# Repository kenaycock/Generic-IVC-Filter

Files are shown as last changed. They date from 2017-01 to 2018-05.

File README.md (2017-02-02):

# Generic-IVC-Filter
*Design of a Generic IVC Filter*

======================

RESOURCES
---------

1. **CAD/** SolidWorks 3D solid models and 2D drawings of the generic IVC filter

2. **Fatigue_coupon/** Placeholder for files relating to fatigue coupon specimens

3. **Preliminary_FEA/** ABAQUS simulation files for predicting fatigue performance of the generic IVC filter

4. **Regulatory-grade_FEA/** Placeholder for final FEA simulation files

5. **.pdf** Further documentation 

CREDIT
------
US FDA: Brent Craven, Jason Weaver, Kenneth Aycock

Confluent Medical (formerly NDC): Tom Duerig, Craig Bonsignore, Karthikeyan Senthilnathan

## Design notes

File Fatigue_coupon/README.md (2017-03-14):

# Fatigue coupon

*Placeholder for files relating to design, manufacture, and testing of fatigue coupons (aka "subcomponent" models)*

- [x] Design fatigue coupon
- [x] Design coupon fixture
- [x] Perform FEA analyses to predict the stresses in the coupon -- do they mimic the *in vivo* loading of the device?
- [x] Generate drawings and DXF for coupon
- [x] Upload files
- [ ] Feedback?

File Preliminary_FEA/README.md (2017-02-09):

# Preliminary FEA

*ABAQUS FEA simulation files*

1. **Input_Files/**   ABAQUS/Standard input files (includes mesh, material properties, boundary conditions, etc.)

2. **ABAQUS_CAE/**   ABAQUS/CAE files used to generate ABAQUS input

3. **Generic_IVC_filter_project_Preliminary_FEA_Summary.pdf**   Brief documentation of preliminary FEA simulation results

Simulations were performed using the same material constants for the ABAQUS Superelastic UMAT as those in  https://github.com/cbonsig/strain-amplitude-volume-fraction/blob/master/Abaqus_6.12-1_Example.inp

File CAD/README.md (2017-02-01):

# CAD

*Directories/Files:*

1. **Rev0** Starting design for generic IVC filter

2. **Rev1** Generic IVC filter following design revision and preliminary FEA analysis. This model needs to be revised now for manufacturing a prototype (adjust kerf, etc.).

3. **Rev1.1** Rev1 modified for manufacturing

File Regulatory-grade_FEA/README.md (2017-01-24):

# Regulatory-grade FEA

*Placeholder for final, "regulatory-grade" FEA simulations*

Todo:
V&V:

1. Verification
  - [ ] Code verification? (i.e., MMS?)
  - [ ] Numerical verification (i.e., grid refinement study)
  - [ ] Material model verification: in collaboration with Confluent Medical, 
    - [ ] obtain lot-specific nitinol material properties
    - [ ] fit constants to raw material testing data 
    
2. Validation
  1. Fatigue testing with sub-component model
    - same material processing history as prototype devices (e.g., heat treating and electropolishing)
  2. Other?

Generic IVCF FEA:

1. Determine final geometry of generic IVC filter
  - [ ] Account for differences between design and manufactured prototypes (tolerances?)
  - [ ] Account for material removed during finishing processes (e.g., electropolishing)
2. Simulate sheathing (prestrain)
3. Simulate placement (contact area/length/forces)
  - [ ] Finalize IVC diameters used to represent variability in human population
4. Valsalva (fatigue)
  - [ ] Finalize boundary conditions (CI=0.5?)

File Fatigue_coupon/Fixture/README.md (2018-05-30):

## Custom fixture used for force-displacement and fatigue tests.

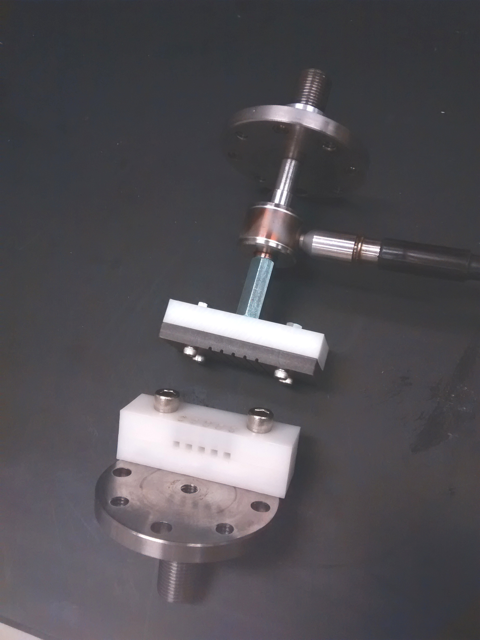
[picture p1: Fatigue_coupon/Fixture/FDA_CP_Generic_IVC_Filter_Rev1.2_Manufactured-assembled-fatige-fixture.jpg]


***Note**: During the experiments, the smooth side of the contact plate (part 5) was used rather than the slotted side due to difficulty alligning the struts with the slots. No lateral motion of the struts was observed during the experiments (confirmed using high-speed video).*

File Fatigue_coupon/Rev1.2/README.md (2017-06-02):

# Fatigue coupons

Experimental plan: 

|                  | <sup>\*</sup>low-strain coupon | <sup>†</sup>high-strain coupon                |
| ---------------- | ----------------- | --------------------------------- |
| strain amplitude | <sup>‡</sup>0.19%, 0.50%      | 0.50%, 0.75%, 1.00%, 1.25%, 1.50% |

<sup>\*</sup>*test to 10<sup>7</sup> cycles*<br>
<sup>†</sup>*fatigue-to-fracture*<br>
<sup>‡</sup>*worst-case physiological conditions, i.e., Valsalva in 28mm IVC*

10 samples per condition:
* 20 low-strain coupons
* 50 high-strain coupons

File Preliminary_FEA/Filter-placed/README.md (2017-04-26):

# Mesh for placed GIVCF

STL meshes for the generic IVC filter placed in a 28 mm-diameter circular vena cava model. 

Virtual filter placement was performed using nonlinear finite element analysis with nitinol material constants from experimental data (see material characterization folder). The vein model was approximated as rigid. 

Dimensions are mm.

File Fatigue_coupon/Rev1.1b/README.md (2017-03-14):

# Rev1.1b

* Proposed fatigue coupon and fatigue fixture assembly
* Equipment: Bose ElectroForce (ELF) 3300
* Tests will be performed inside a fluid bath at 37°C

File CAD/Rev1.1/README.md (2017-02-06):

# Rev1.1

**Rev1 filter revised for manufacturability**

REVISIONS
---------
- [x] Account for
    1. laser beam cutting width (kerf) and
    2. material removal related to surface finishing (see *Open Stent* manuscript from C. Bonsignore for details)
- [x] Change the tubing from TSE0800X0525GS to TSE0800X0515GS to increase the wall thickness and compensate for material removed during surface finishing
    * same OD, new ID (1.3081mm here vs. 1.3335mm in Rev1; see https://shop.confluentmedical.com/collections/tube)
- [x] Add a flat configuration for the laser toolpath
- [x] Improve the drawing sheets
- [x] Create 2D "dxf" file for the laser toolpath (scale is 1:1)

NOTES
-----
* The following values were assumed based on those given in the *Open Stent* manuscript:
    * Laser kerf: ~~0.025mm~~ 0.050mm
    * Material removal during finishing
        * width: ~~0.036mm (i.e., 0.018mm from each side)~~ 0.025mm (i.e., 0.0125mm from each side)
        * thickness: ~~0.059mm (from *inside* surface to remove draw lines)~~ **TBD; measure finished prototypes**

CORRESPONDENCE
--------------
See https://github.com/kenaycock/Generic-IVC-Filter/issues/2

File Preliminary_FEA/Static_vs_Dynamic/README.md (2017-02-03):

# Static vs Dynamic

*Demonstration of a case where the static solver diverges while the dynamic solver converges:*

**Boundary conditions during Valsalva:**
  - Filter hub: **translation constrained in 'y' and 'z', but not in the axial direction, 'x'.**
  - Plate: fixed displacement representing reduction in the minor diameter of the IVC during the Valsalva maneuver
  - Distal end of filter strut: unconstrained, but there is a contact interaction between the strut surface and the plate that represents the vein wall.
    - Tangential friction is set relatively high (0.2); distal end of filter strut *"rocks"* along plate surface
  - **Files:**
    1. ...Static_BCs1.inp (diverges during step 3, 'valsalva1') 
    2. ...Dynamic_BCs1.inp 

<br><br>
*If the boundary conditions are tweaked slightly, the static simulation converges:*

**Boundary conditions during Valsalva:**
  - Filter hub: **translation constrained in 'x', 'y' and 'z' directions.**
  - Plate: fixed displacement representing reduction in the minor diameter of the IVC during the Valsalva maneuver
  - Distal end of filter strut: unconstrained, but there is a contact interaction (including tangential friction) between the strut surface and the plate that represents the vein wall.
    - Tangential friction is set relatively low (0.02); distal end of filter strut *slides* along plate surface
  - **Files:**
    1. ...Static_BCs2.inp
    
<br><br>
CORRESPONDENCE
--------------
**Feedback from Karthik:**
  - Static solver will not converge when there is unconstrained rigid body motion. Adjust boundary conditions accordingly in the future, or use Dynamic/Implicit and ensure that kinetic energy is a small (\<\<1%) fraction of the total internal energy.

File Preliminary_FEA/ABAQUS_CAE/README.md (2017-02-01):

# ABAQUS CAE files

1. **...cae/jnl** ABAQUS/CAE files for preliminary FEA simulations
2. **GIVCF_Rev1.STEP**   3D solid CAD model of the generic IVC filter (exported from SolidWorks); used to generate the finite element meshes in ABAQUS/CAE

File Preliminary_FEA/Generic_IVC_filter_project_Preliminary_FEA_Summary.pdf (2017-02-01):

# Design of a Generic IVC Filter

2/1/2017

Generic IVC Filter Critical Path Project
Kenny Aycock, Jason Weaver and Brent Craven (FDA)
Craig Bonsignore and Tom Duerig (Confluent Medical) | 1

# Summary of Preliminary FEA

# FEA performed to evaluate filter design

### Setup:

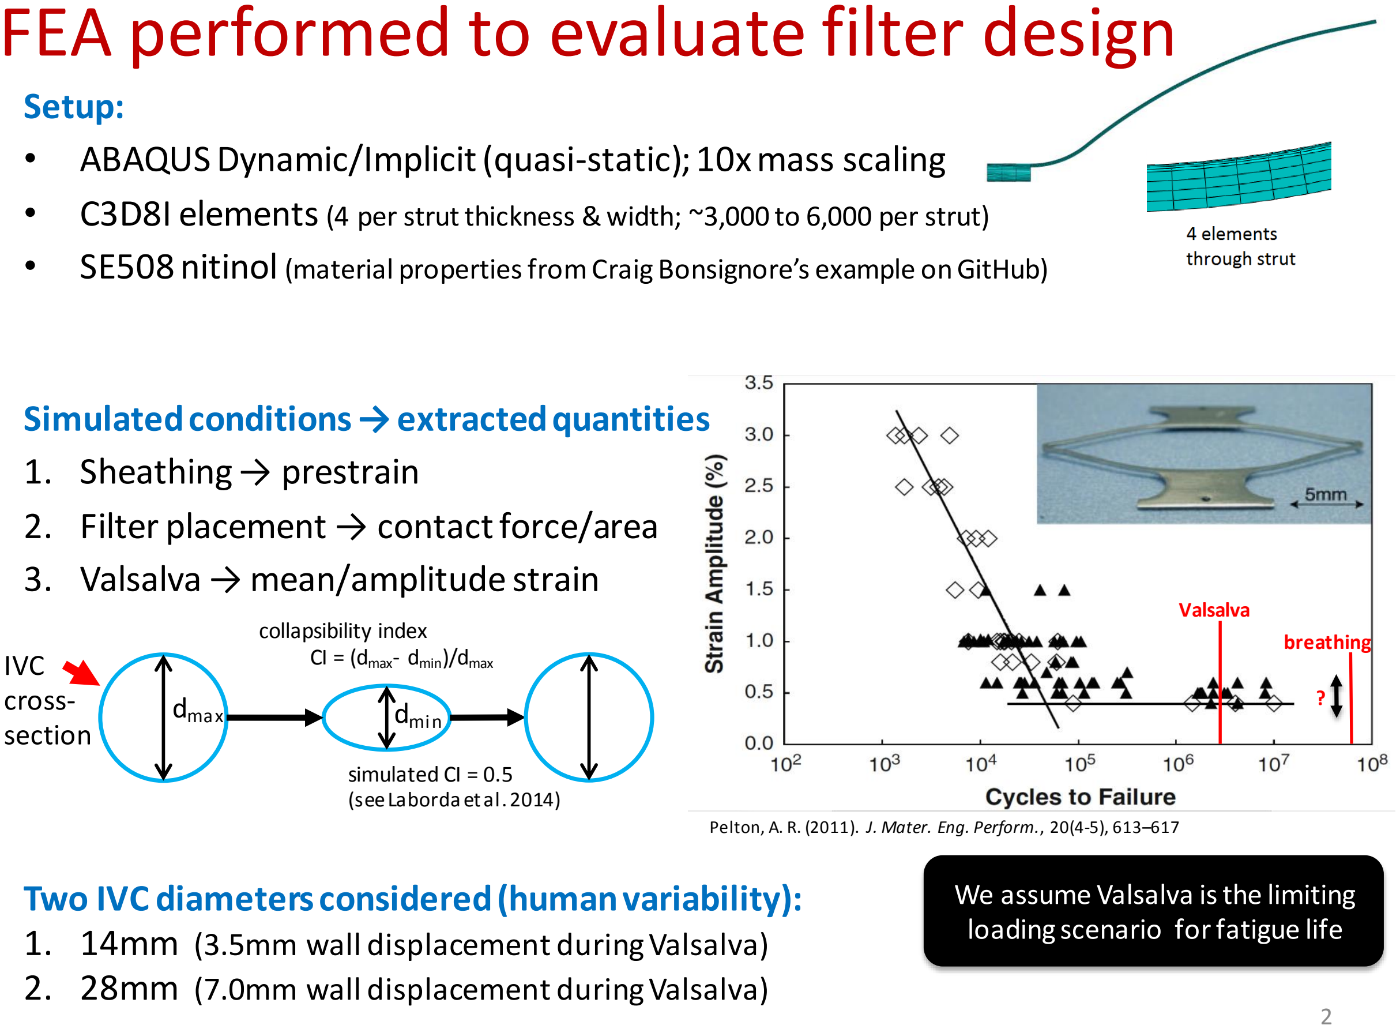
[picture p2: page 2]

breathing

Valsalva

Pelton, A. R. (2011). J. Mater. Eng. Perform., 20(4-5), 613–617

?

simulated CI = 0.5
(see Laborda et al. 2014)

collapsibility index
CI = (dmax- dmin)/dmax IVC
cross-section

dmin dmax

### - ABAQUS Dynamic/Implicit (quasi-static); 10x mass scaling

- C3D8I elements(4 per strut thickness & width; ~3,000 to 6,000 per strut)
- SE508 nitinol (material properties from Craig Bonsignore’s example on GitHub)

### Simulated conditions → extracted quantities 1. Sheathing → prestrain 2. Filter placement → contact force/area 3. Valsalva → mean/amplitude strain

### Two IVC diameters considered (human variability):

1. 14mm (3.5mm wall displacement during Valsalva)
2. 28mm (7.0mm wall displacement during Valsalva)

We assume Valsalva is the limiting loading scenario for fatigue life

# Performance goals are set for quantities extracted from FEA simulations

| distal end contacts wall? | prestrain (max/min prin. LE) | contact force (N) (per strut) | contact area (mm²) (per strut) | ε amplitude, Valsalva (CI=0.5) | mean ε, Valsalva (CI=0.5)
target | yes | <6% | 0.010 to 0.100 | >0.05? | <0.4% | <6%

*to avoid plastic
deformation
during sheathing

# Stress-strain history diagram (Rev1)

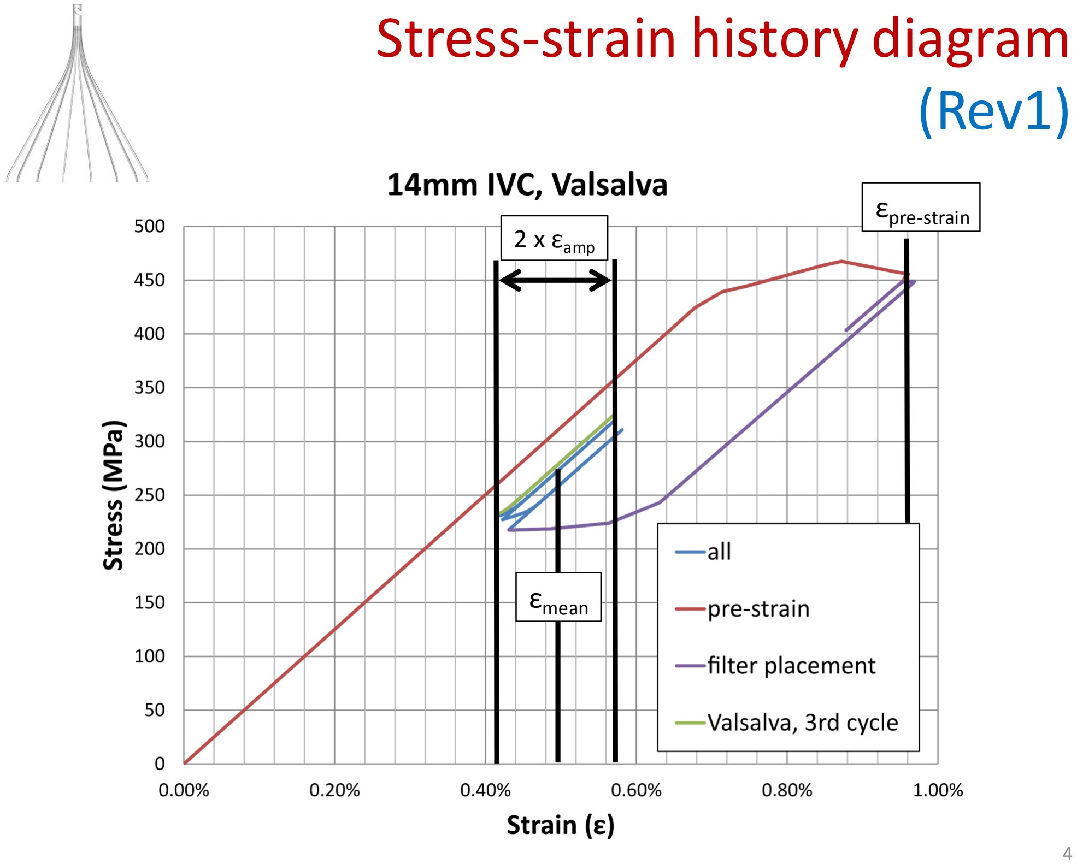
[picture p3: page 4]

εpre-strain
2 x εamp

εmean

### contact point(s)

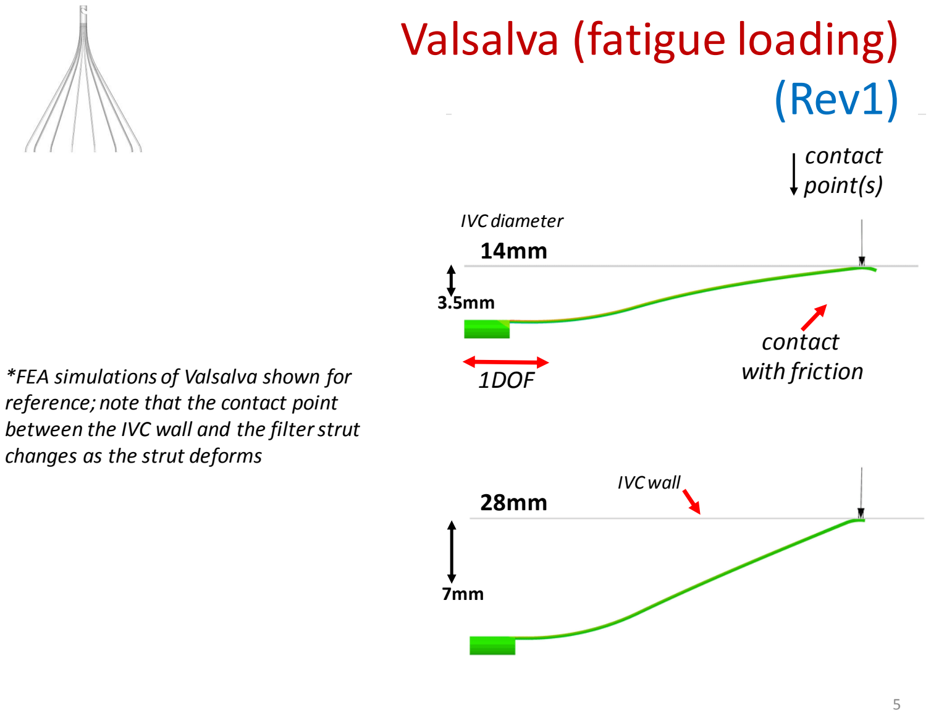
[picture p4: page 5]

### 1DOF

### contact with friction

*FEA simulations of Valsalva shown for reference; note that the contact point between the IVC wall and the filter strut changes as the strut deforms
IVC wall

7mm

3.5mm

28mm

IVC diameter
14mm

# Valsalva (fatigue loading) (Rev1)

## Valsalva

## Filter Placement

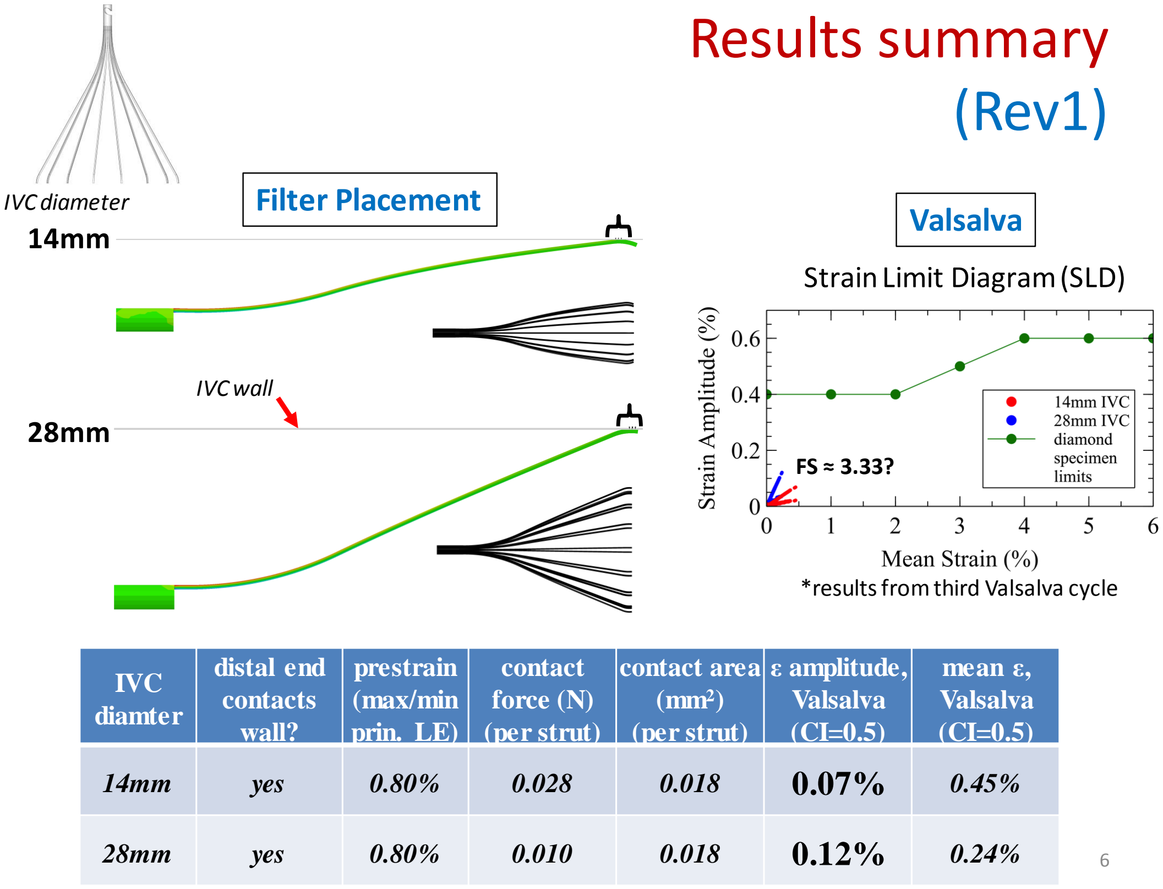
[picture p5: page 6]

28mm

IVC diameter
14mm
IVC diamter | distal end contacts wall? | prestrain (max/min prin. LE) | contact force (N) (per strut) | contact area (mm²) (per strut) | ε amplitude, Valsalva (CI=0.5) | mean ε, Valsalva (CI=0.5)
14mm | yes | 0.80% | 0.028 | 0.018 | 0.07% | 0.45%
28mm | yes | 0.80% | 0.010 | 0.018 | 0.12% | 0.24%

*results from third Valsalva cycle

### Strain Limit Diagram (SLD)

IVC wall

# Results summary (Rev1)

FS ≈ 3.33?

IVC diamter | distal end contacts wall? | prestrain (max/min prin. LE) | contact force (N) (per strut) | contact area (mm²) (per strut) | ε amplitude, Valsalva (CI=0.5) | mean ε, Valsalva (CI=0.5)
coarse (4x4) | yes | 0.80% | 0.0096 | 0.018 | 0.121% | 0.24%
medium (8x8) | yes | 0.92% | 0.0096 | 0.0048 | 0.134% | 0.26%

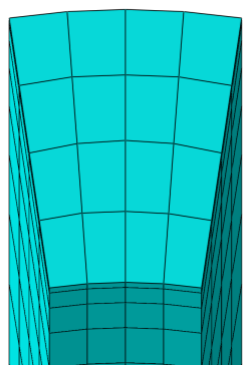
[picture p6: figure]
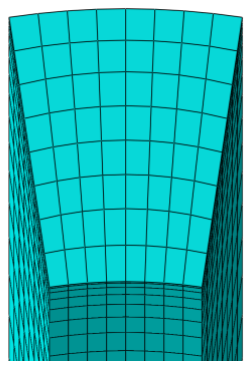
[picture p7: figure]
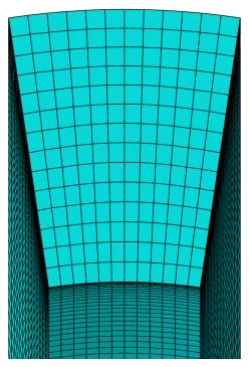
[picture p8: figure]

fine (12x12) | yes | 1.04% | 0.0102 | 0.0050 | 0.139% | 0.27%

# Mesh refinement (Rev1)

## GCI: -2.81%

coarse | medium | fine

IVC diamter | distal end contacts wall? | prestrain (max/min prin. LE) | contact force (N) (per strut) | contact area (mm² ) (per strut) | ε amplitude, Valsalva (CI=0.5) | mean ε, Valsalva (CI=0.5)
28mm | yes | 0.80% | 0.010 | 0.018 | 0.12% | 0.24%
28mm | yes | 0.80% | 0.0086 | 0.0091 | 0.14% | 0.26%

# Eccentric loading of filter strut (Rev1)

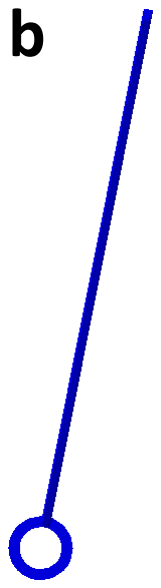
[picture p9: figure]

a | b

a

b

IVC diamter | distal end contacts wall? | prestrain (max/min prin. LE) | contact force (N) (per strut) | contact area (mm²) (per strut) | ε amplitude, Valsalva (CI=0.5) | mean ε, Valsalva (CI=0.5)
28mm | yes | 0.798% | 0.00884 | 0.0182 | 0.122% | 0.239%

# Static/Implicit vs. Dynamic/Implicit (Rev1)

### Static/Imp

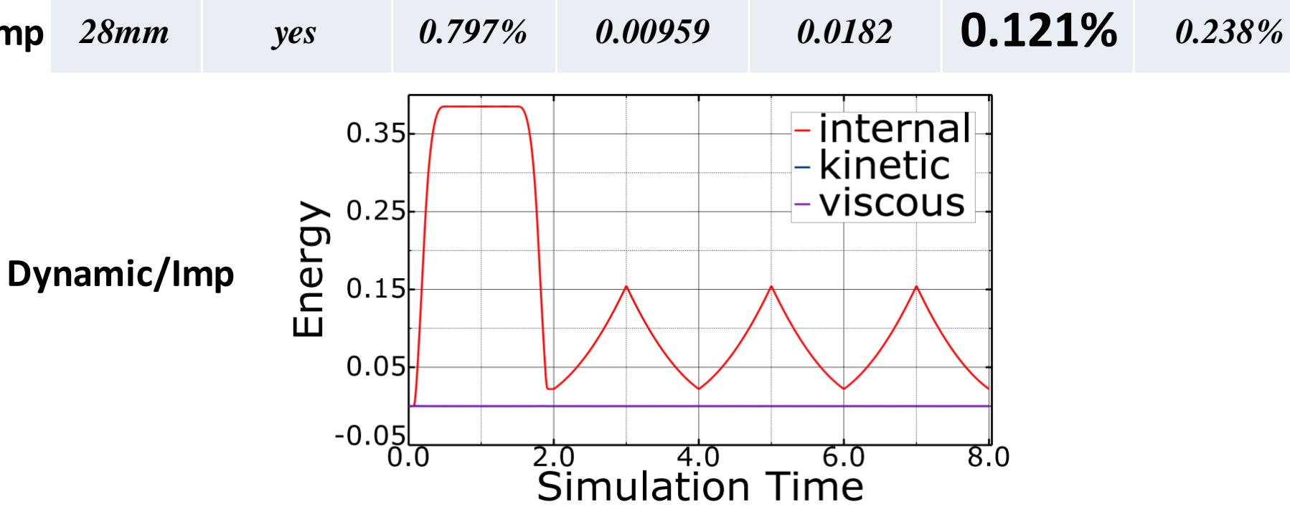
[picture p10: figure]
yes; Dynamic/Imp

### Dynamic/Imp

*Simulations were performed using Abaqus Standard, Dynamic/Implicit to increase stability of contact interactions. Simulations performed using Static/Implicit yield similar results, but do not converge in some cases.

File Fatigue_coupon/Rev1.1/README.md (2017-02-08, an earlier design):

# Rev1.1 Fatigue Coupon

**Fatigue coupon corresponding to the Rev1.1 full device CAD model**

NOTES
-----
* The total length of the strut for the coupon is 16mm (versus 41mm for the full device); this allows us to operate the fatigue tests at a higher frequency
* The mean/amplitude strain point cloud for the coupon matches the point cloud for the full device relatively well (**quantify this**) with a prescribed tip displacement of 1.0mm
* The fatigue coupon design assumes the same amount of material removal for the finishing processes:
    * width: 0.025mm (i.e., 0.0125mm from each side)
    * thickness: **TBD; measure finished prototypes**

CORRESPONDENCE
--------------

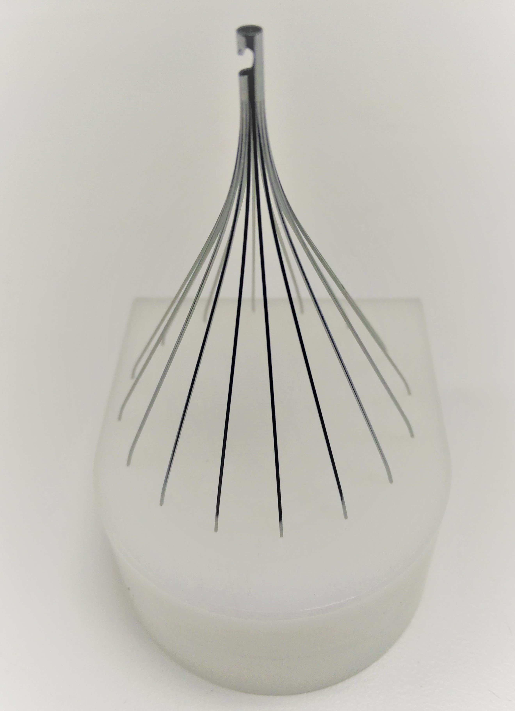
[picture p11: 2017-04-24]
CAD/Rev1.1/Prototype/FDA-filter-prototype-20170322-02.jpg

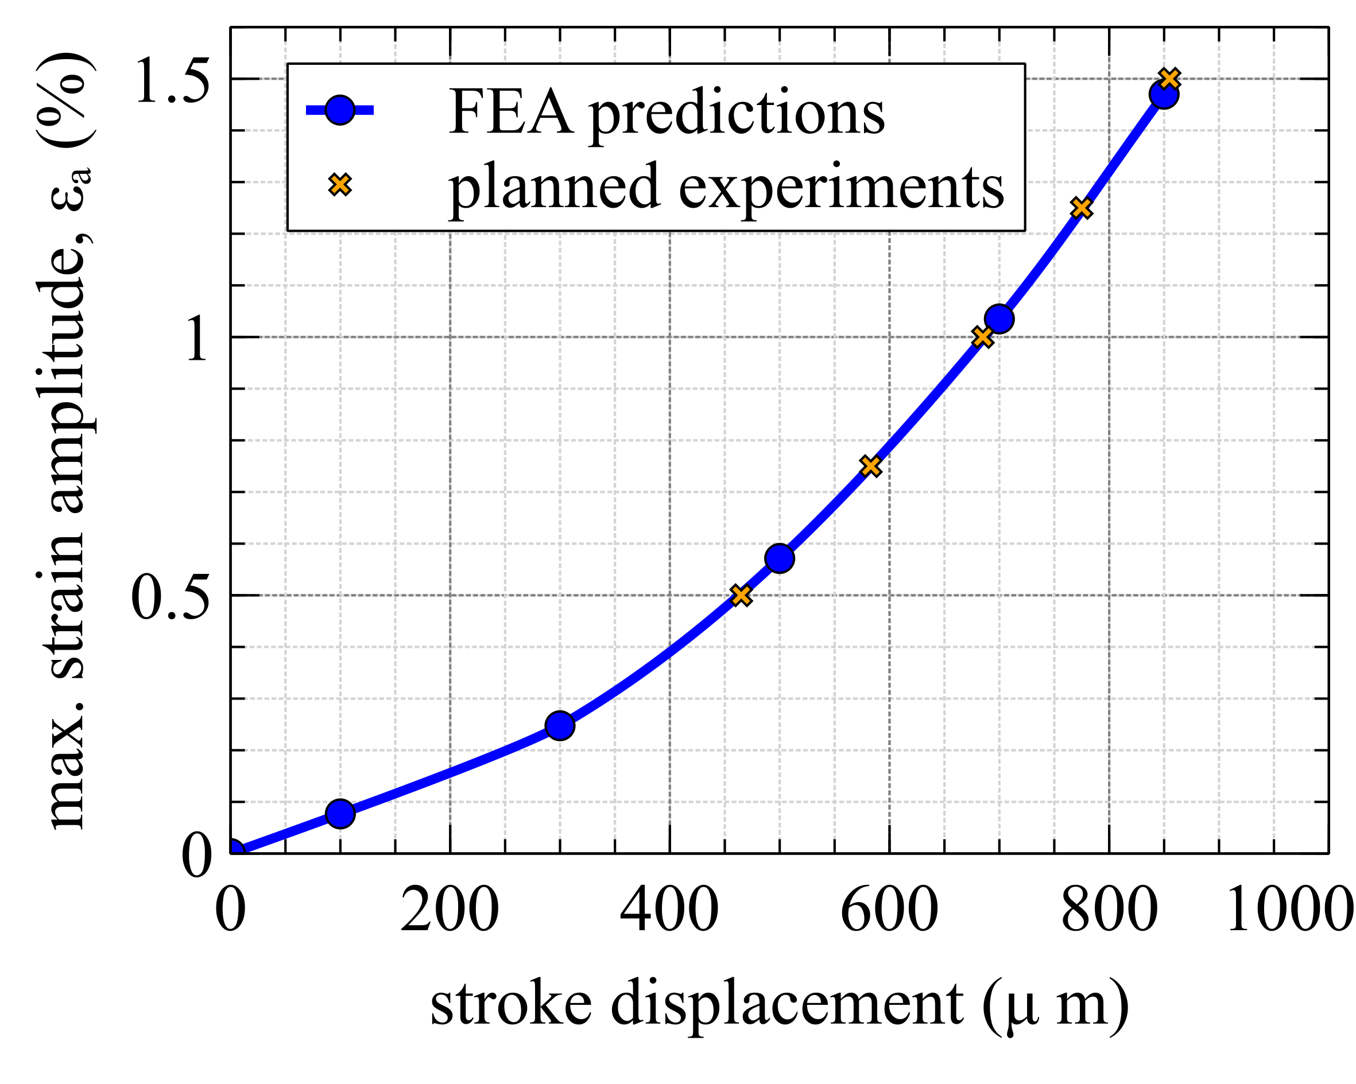
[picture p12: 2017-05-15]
Fatigue_coupon/Rev1.2/02_high-strain_fatigue_coupon/02b_high-strain_fatigue_coupon_strain_amp_vs_stroke_displacement.png

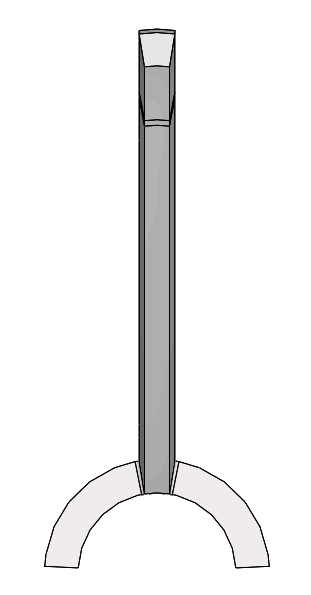
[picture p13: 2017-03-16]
Fatigue_coupon/Rev1.1b/Additional_views/Fatigue_coupon_Rev1.1b_02_Bottom_View.png

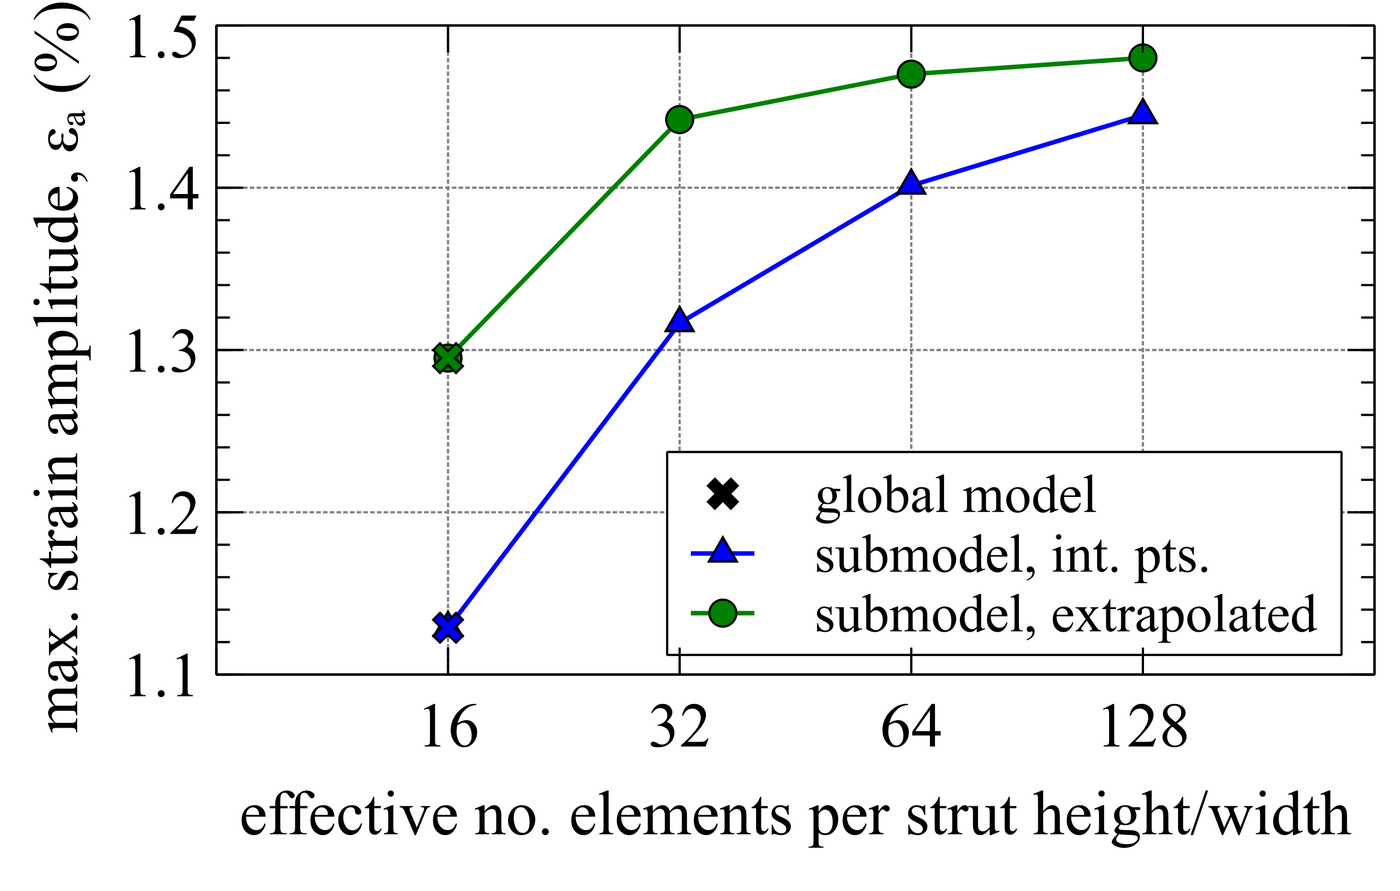
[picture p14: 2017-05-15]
Fatigue_coupon/Rev1.2/02_high-strain_fatigue_coupon/02a_high-strain_fatigue_coupon_FEA_mesh_refinement.png

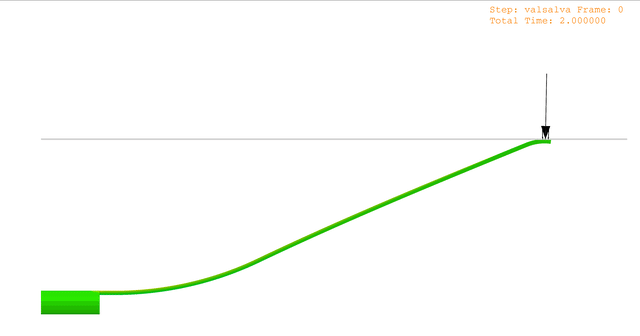
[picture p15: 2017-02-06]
Preliminary_FEA/Animations/GIVCF_Valsalva_28mm_IVCD.gif

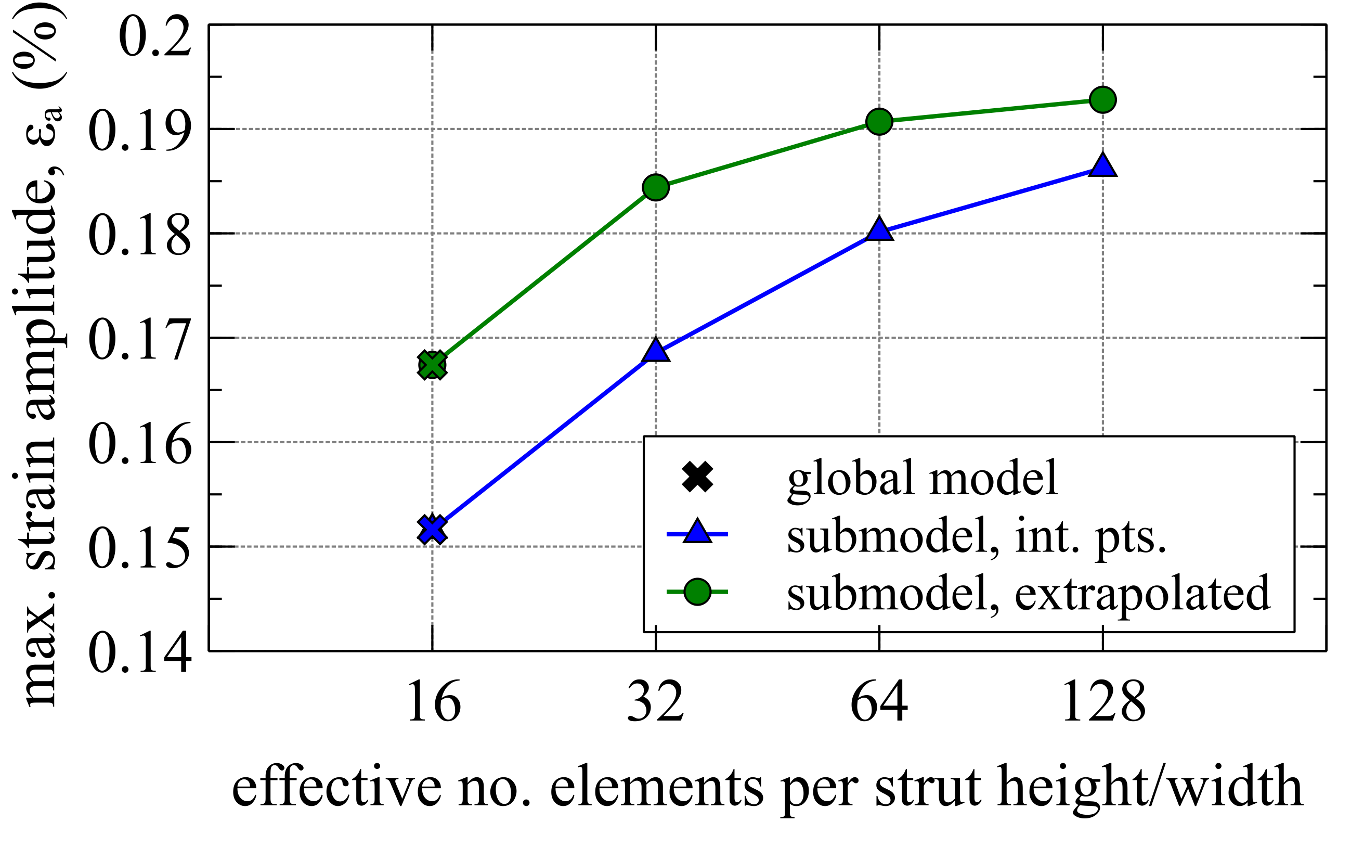
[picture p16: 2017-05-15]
Fatigue_coupon/Rev1.2/01_low-strain_fatigue_coupon/01a_low-strain_fatigue_coupon_FEA_mesh_refinement.png

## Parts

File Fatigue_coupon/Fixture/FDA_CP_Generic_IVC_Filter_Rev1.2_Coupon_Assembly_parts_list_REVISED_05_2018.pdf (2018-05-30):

Fatigue fixture assembly for testing generic IVC filter fatigue coupons
Kenneth Aycock
5/30/17
Revised for confluent: 5/30/ 18 | Part number
Part | (assembly drawing) | McMaster # | Price | Quantity | Total
Equipment:
BOSE ELF 3300 | 1
Honeywell 22N force transducer | 2
Transducer adapter | 3

Custom parts (to be machined):
Upper plate 1 (delrin) | 4
Upper plate 2 (in contact with struts; slippery delrin) | 5
Bottom plate 1 (delrin) | 6
Bottom plate 2 (delrin) | 7

McMaster parts:
1" x 24" x 3/8" Delrin bar, tight-tolerance | (4, 6, 7) | 9123K76 (2ft) | $5.70 | 1 | $5.70
6" x 6" x 1/4" slippery Delrin sheet (13% PTFE) | (5) | 8578K412 | $35.80 | 1 | $35.80
Threaded hex standoff, 3/8" OD, 1" lg, #10-32 thread (Zinc-plated) | 8a | 91920A300 | $2.57 | N/A
Threaded hex standoff, 3/8" OD, 1" lg, #10-32 thread (Stainless) | 8b | 91115A300 | $3.49 | 1 | $3.49
0.051" dia piano wire (36 ft) | 9a | 8908K56 | $11.86 | N/A
3/64" dowel pins (50 cnt.) | 9b | 97155A115 | $3.27 | 1 | $3.27
#2-56 stainless steel set screws (5 cnt.) | 10 | 92313A022 | $5.38 | 3 | $16.14

#6-32 x 3/4" corrosion resist cap screws (25 cnt.) | 11 | 91274A020 | $9.06 | 1 | $9.06

#6-32 corrosion resist hex nuts (100 cnt.) | 12 | 90480A007 | $1.24 | 1 | $1.24

#10-32 x 3/4" corrsion resist cap screws (50 cnt.) | 13 | 91274A174 | $8.87 | 1 | $8.87

1/4" - 20 x 1 1/4" lg. corrosion resist cap screws (25 cnt.) | 14 | 90128A376 | $7.05 | 1 | $7.05

( ): raw materials
used in preliminary tests only | | | | Total: | $90.62
suggested replacement due to corrosion in PBS bath

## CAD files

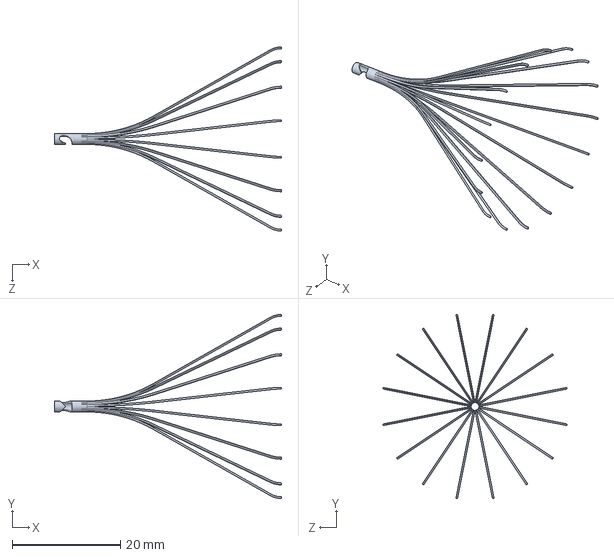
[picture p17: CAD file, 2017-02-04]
CAD/Rev1.1/FDA_CP_Generic_IVC_Filter_Rev1.1.SLDPRT
42.0 x 34.1 x 34.1 mm

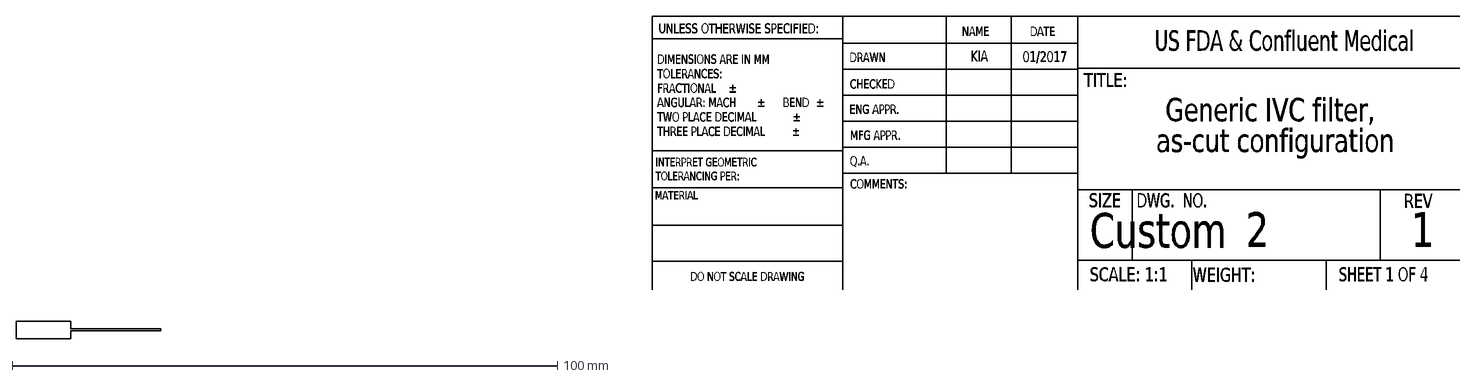
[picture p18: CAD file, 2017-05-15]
Fatigue_coupon/Rev1.2/01_low-strain_fatigue_coupon/01_low-strain-coupon.DXF
Generic IVC filter,
as-cut configuration
1
DO NOT SCALE DRAWING
2
SHEET 1 OF 4
01/2017
KIA
UNLESS OTHERWISE SPECIFIED:
SCALE: 1:1
WEIGHT:
REV
DWG. NO.
Custom
SIZE
TITLE:
US FDA & Confluent Medical
NAME
DATE
COMMENTS:
Q.A.
MFG APPR.
ENG APPR.
CHECKED
DRAWN
MATERIAL
INTERPRET GEOMETRIC
TOLERANCING PER:
DIMENSIONS ARE IN MM
TOLERANCES:
FRACTIONAL
±
ANGULAR: MACH
BEND
TWO PLACE DECIMAL
THREE PLACE DECIMAL

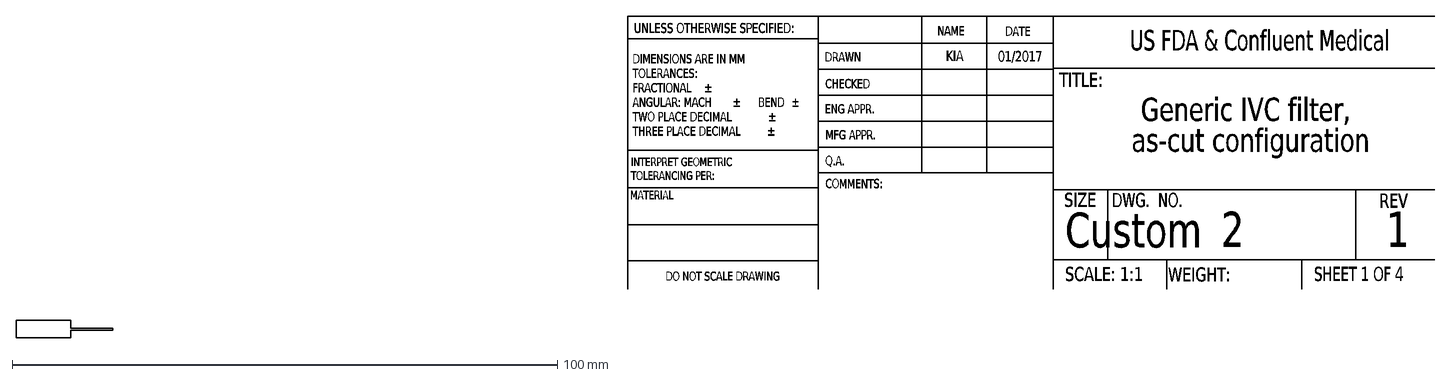
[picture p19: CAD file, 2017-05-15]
Fatigue_coupon/Rev1.2/02_high-strain_fatigue_coupon/02_high-strain-coupon.DXF
Generic IVC filter,
as-cut configuration
1
DO NOT SCALE DRAWING
2
SHEET 1 OF 4
01/2017
KIA
UNLESS OTHERWISE SPECIFIED:
SCALE: 1:1
WEIGHT:
REV
DWG. NO.
Custom
SIZE
TITLE:
US FDA & Confluent Medical
NAME
DATE
COMMENTS:
Q.A.
MFG APPR.
ENG APPR.
CHECKED
DRAWN
MATERIAL
INTERPRET GEOMETRIC
TOLERANCING PER:
DIMENSIONS ARE IN MM
TOLERANCES:
FRACTIONAL
±
ANGULAR: MACH
BEND
TWO PLACE DECIMAL
THREE PLACE DECIMAL

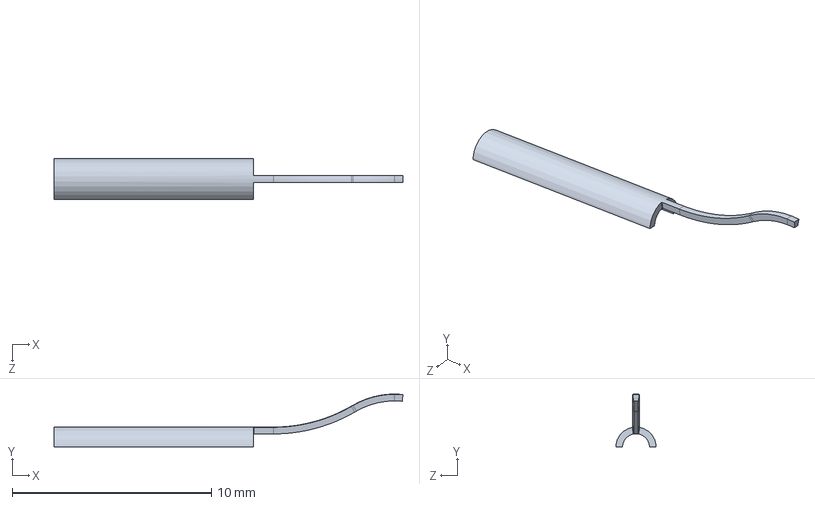
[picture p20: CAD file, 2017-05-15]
Fatigue_coupon/Rev1.2/FDA_CP_Generic_IVC_Filter_Rev1.2_PROTO_DIMS_All-in-one.SLDPRT
17.5 x 2.66 x 2.03 mm

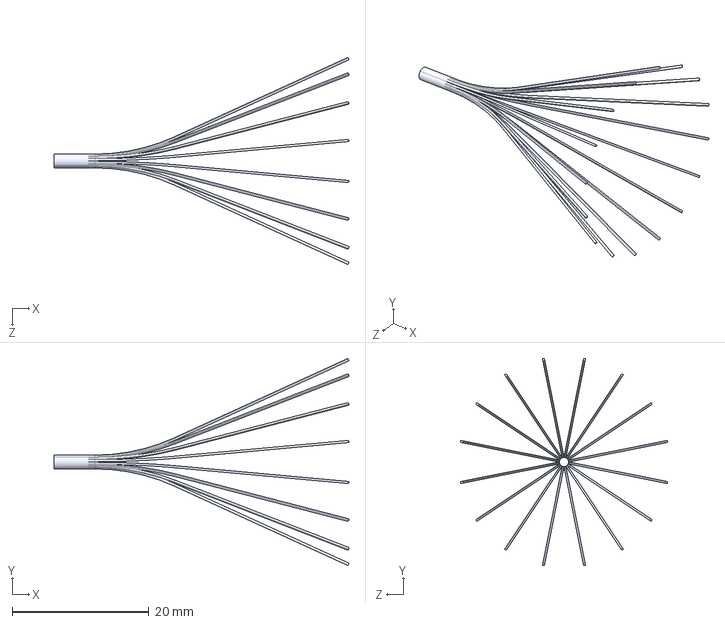
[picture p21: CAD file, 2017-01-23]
Preliminary_FEA/ABAQUS_CAE/GIVCF_Rev1.STEP
43.1 x 30.3 x 30.3 mm

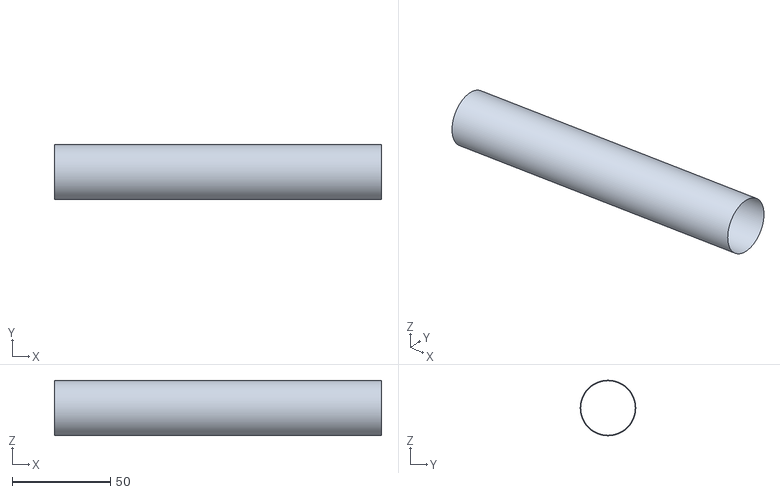
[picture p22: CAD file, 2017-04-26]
Preliminary_FEA/Filter-placed/IVC_28mm_dia.stl
166.4 x 28.0 x 28.0

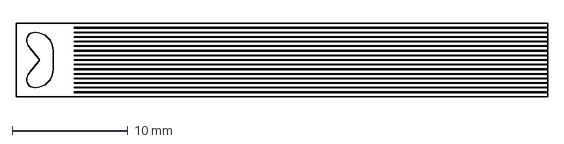
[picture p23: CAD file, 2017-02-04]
CAD/Rev1.1/FDA_CP_Generic_IVC_Filter_Rev1.1_Laser_template.DXF
46.0 x 6.38 mm

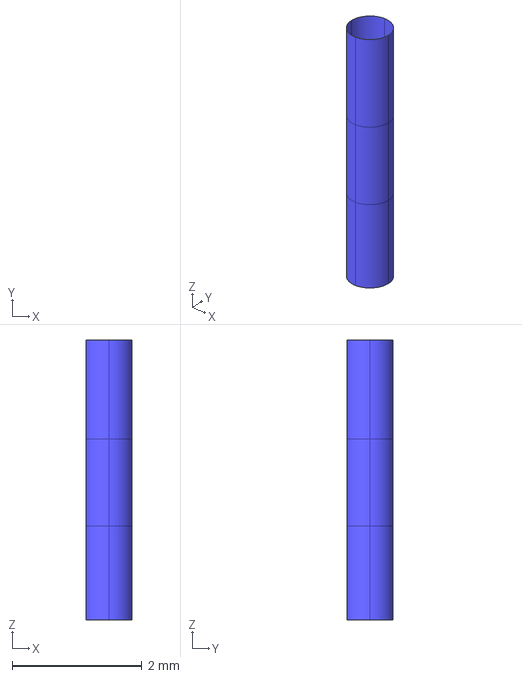
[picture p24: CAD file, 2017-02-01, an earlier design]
CAD/Rev0/Mock-IVC-Lumen.iges
0.711 x 0.711 x 4.32 mm

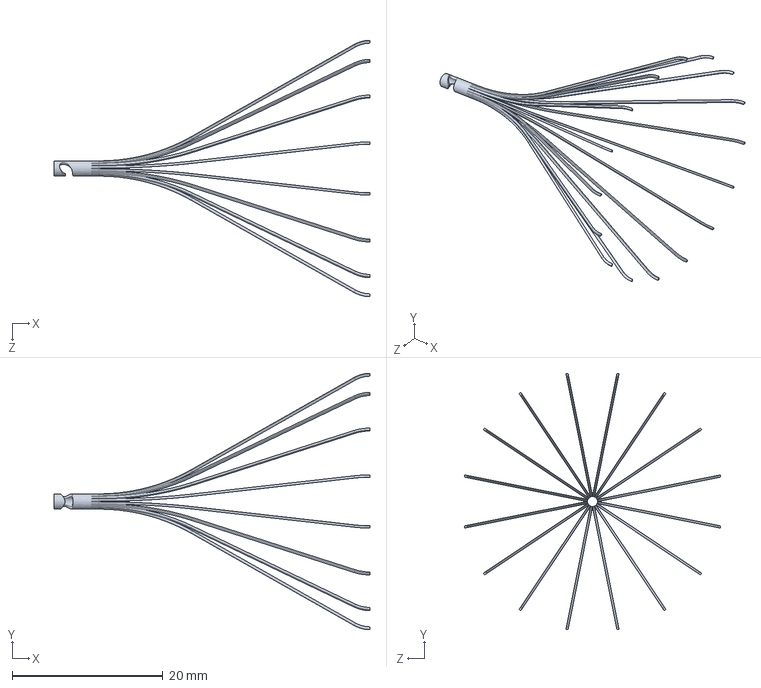
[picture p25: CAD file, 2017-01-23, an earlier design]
CAD/Rev1.0/FDA_CP_Generic_IVC_Filter_Rev1.SLDPRT
42.0 x 34.1 x 34.1 mm

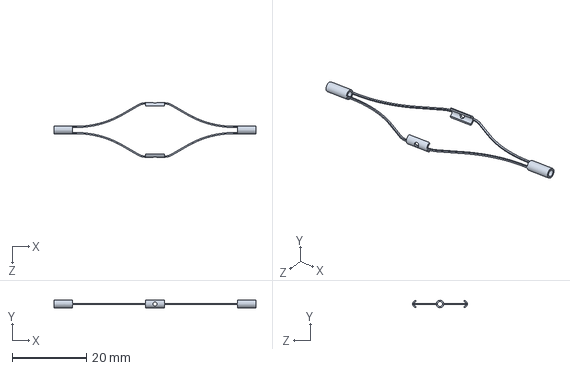
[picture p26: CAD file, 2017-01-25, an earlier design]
Fatigue_coupon/Rev1.0/FDA_CP_Generic_IVC_Filter_Rev1_Fatigue_Coupon.SLDPRT
54.3 x 2.03 x 14.7 mm

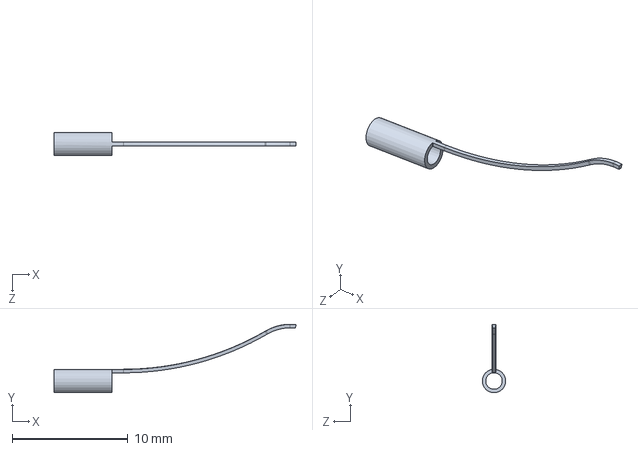
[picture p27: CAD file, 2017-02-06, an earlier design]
Fatigue_coupon/Rev1.1/FDA_CP_Generic_IVC_Filter_Rev1.1_Coupon.SLDPRT
20.9 x 5.92 x 2.03 mm

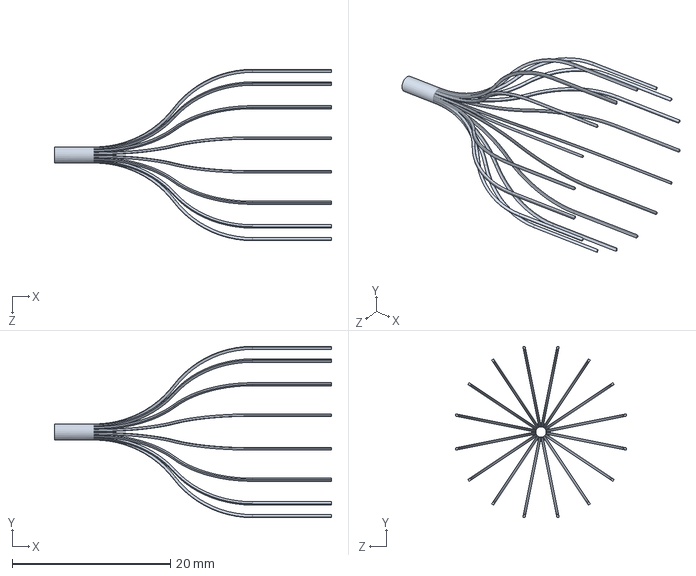
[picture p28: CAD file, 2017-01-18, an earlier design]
CAD/Rev0/FDA_CP_Generic_IVC_Filter_Rev0.SLDPRT
35.0 x 21.6 x 21.6 mm

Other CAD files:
CAD/Rev1.0/FDA_CP_Generic_IVC_Filter_Rev1.SLDDRW
CAD/Rev1.1/FDA_CP_Generic_IVC_Filter_Rev1.1.SLDDRW
Fatigue_coupon/Rev1.1/FDA_CP_Generic_IVC_Filter_Rev1.1_Coupon.DXF
Fatigue_coupon/Rev1.1/FDA_CP_Generic_IVC_Filter_Rev1.1_Coupon.SLDDRW
Fatigue_coupon/Rev1.2/01_low-strain_fatigue_coupon/FDA_CP_Generic_IVC_Filter_Rev1.2_low-strain-coupon.SLDDRW
Fatigue_coupon/Rev1.2/02_high-strain_fatigue_coupon/FDA_CP_Generic_IVC_Filter_Rev1.2_high-strain-coupon.SLDDRW

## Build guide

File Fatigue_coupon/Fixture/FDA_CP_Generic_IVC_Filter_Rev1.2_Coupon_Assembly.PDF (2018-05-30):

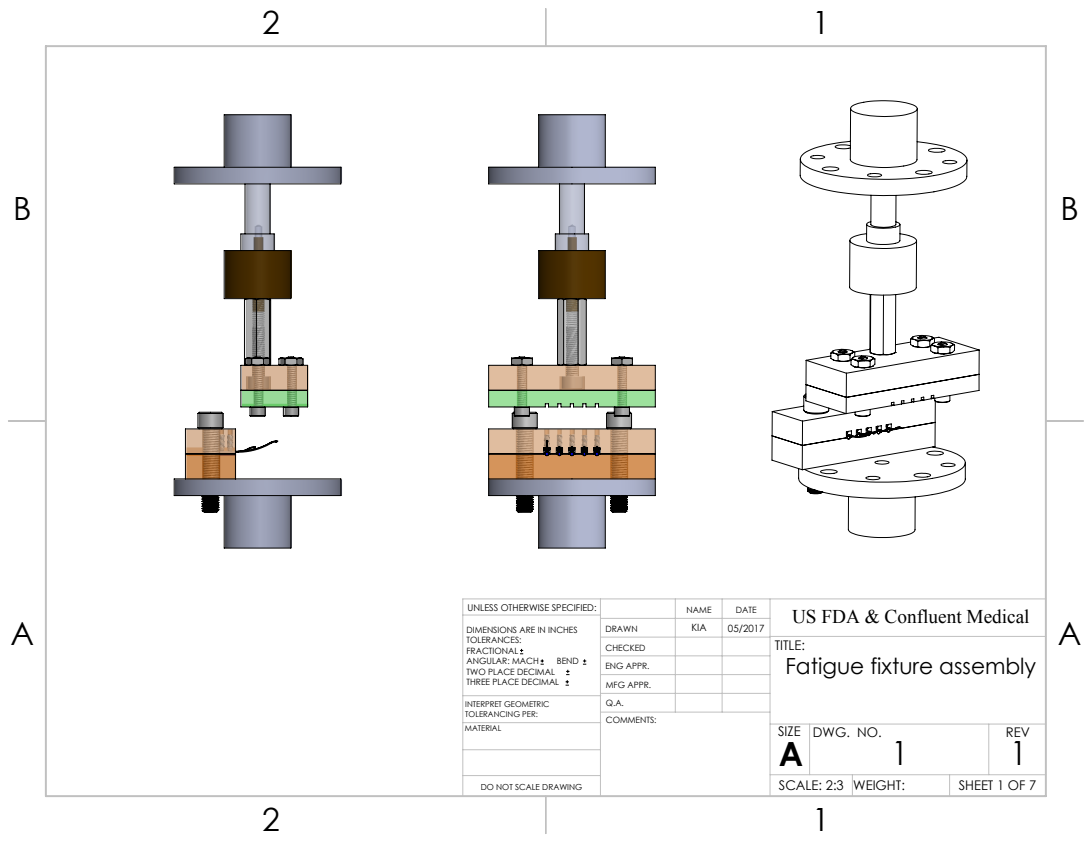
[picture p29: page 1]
SHEET 1 OF 7; SCALE: 2:3; WEIGHT:; DWG. NO.; REV

UNLESS OTHERWISE SPECIFIED: | | | DATE | US FDA & Confluent Medical NAME
DIMENSIONS ARE IN INCHES TOLERANCES: FRACTIONAL ANGULAR: MACH BEND TWO PLACE DECIMAL THREE PLACE DECIMAL | DRAWN | KIA | 05/2017

CHECKED | | | TITLE: Fatigue fixture assembly

ENG APPR.
MFG APPR.

INTERPRET GEOMETRIC TOLERANCING PER: | Q.A.

DO NOT SCALE DRAWING

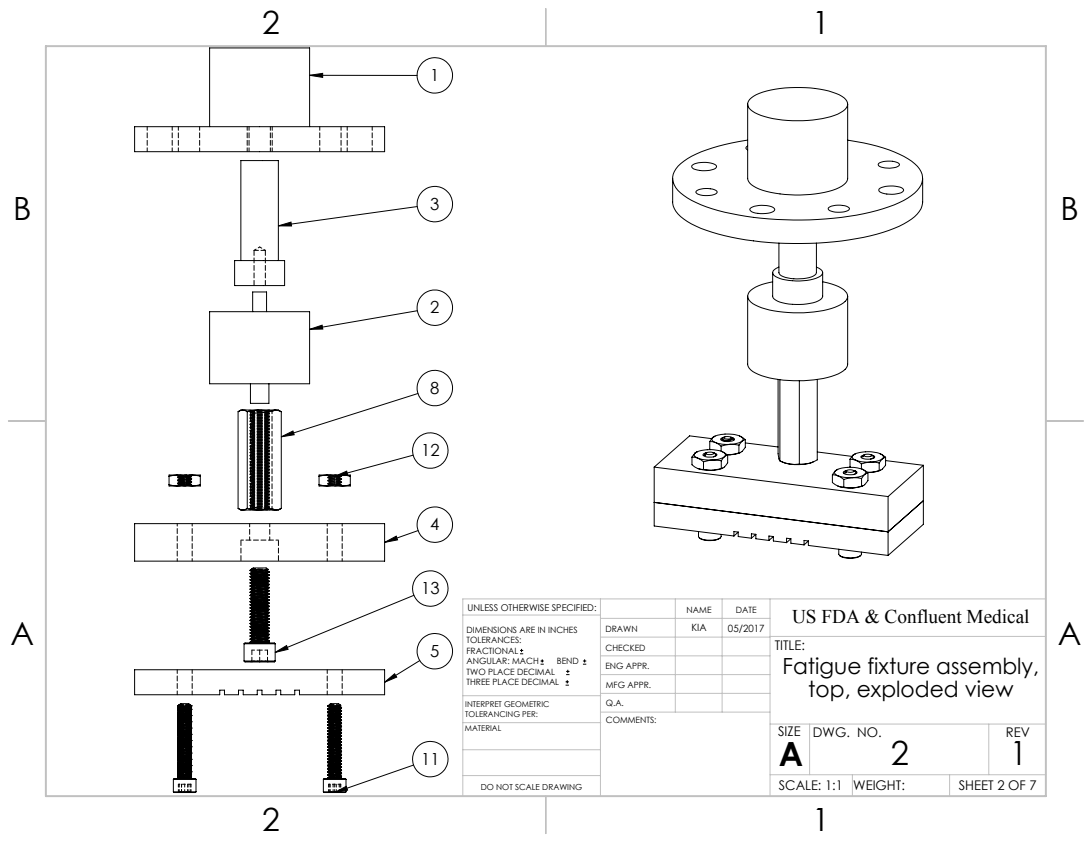
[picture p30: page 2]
SCALE: 1:1; WEIGHT:; DWG. NO.; REV

UNLESS OTHERWISE SPECIFIED: | | | DATE | US FDA & Confluent Medical NAME
DIMENSIONS ARE IN INCHES TOLERANCES: FRACTIONAL ANGULAR: MACH BEND TWO PLACE DECIMAL THREE PLACE DECIMAL | DRAWN | KIA | 05/2017

CHECKED | | | TITLE: Fatigue fixture assembly, top, exploded view

ENG APPR.
MFG APPR.

INTERPRET GEOMETRIC TOLERANCING PER: | Q.A.

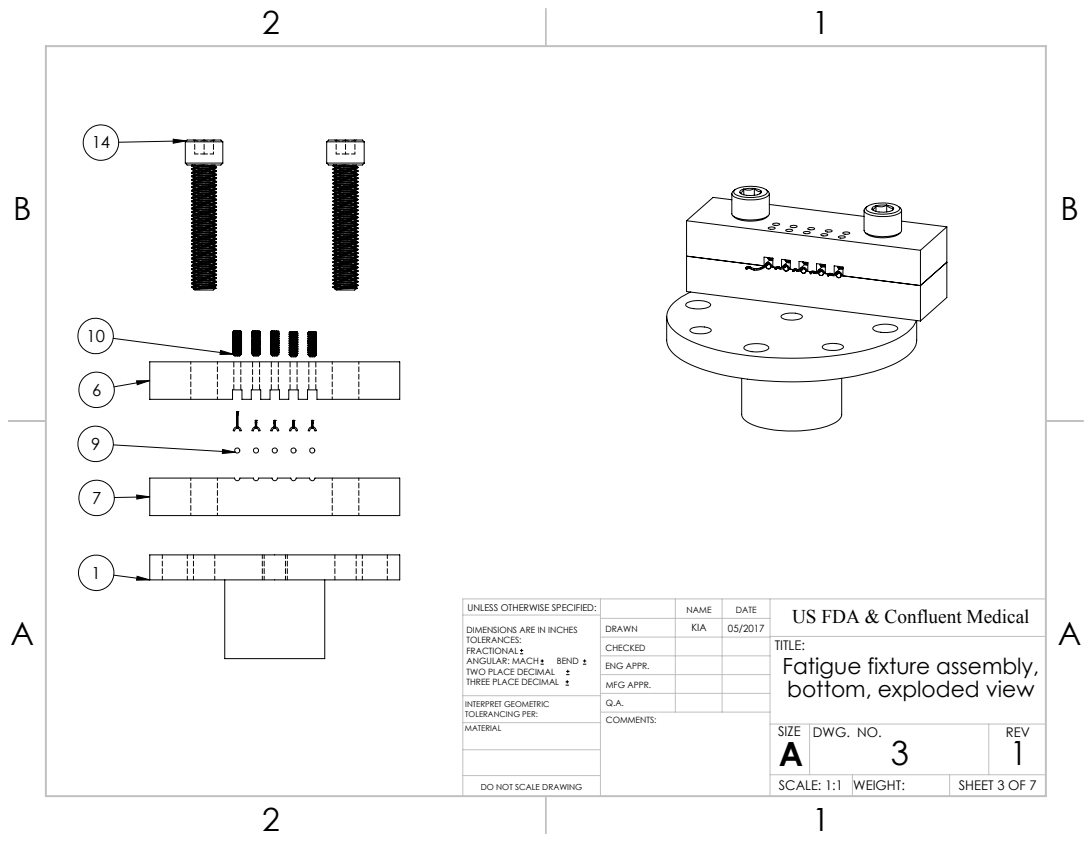
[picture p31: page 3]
SCALE: 1:1; WEIGHT:; DWG. NO.; REV

UNLESS OTHERWISE SPECIFIED: | | | DATE | US FDA & Confluent Medical NAME
DIMENSIONS ARE IN INCHES TOLERANCES: FRACTIONAL ANGULAR: MACH BEND TWO PLACE DECIMAL THREE PLACE DECIMAL | DRAWN | KIA | 05/2017

CHECKED | | | TITLE: Fatigue fixture assembly, bottom, exploded view

ENG APPR.
MFG APPR.

INTERPRET GEOMETRIC TOLERANCING PER: | Q.A.

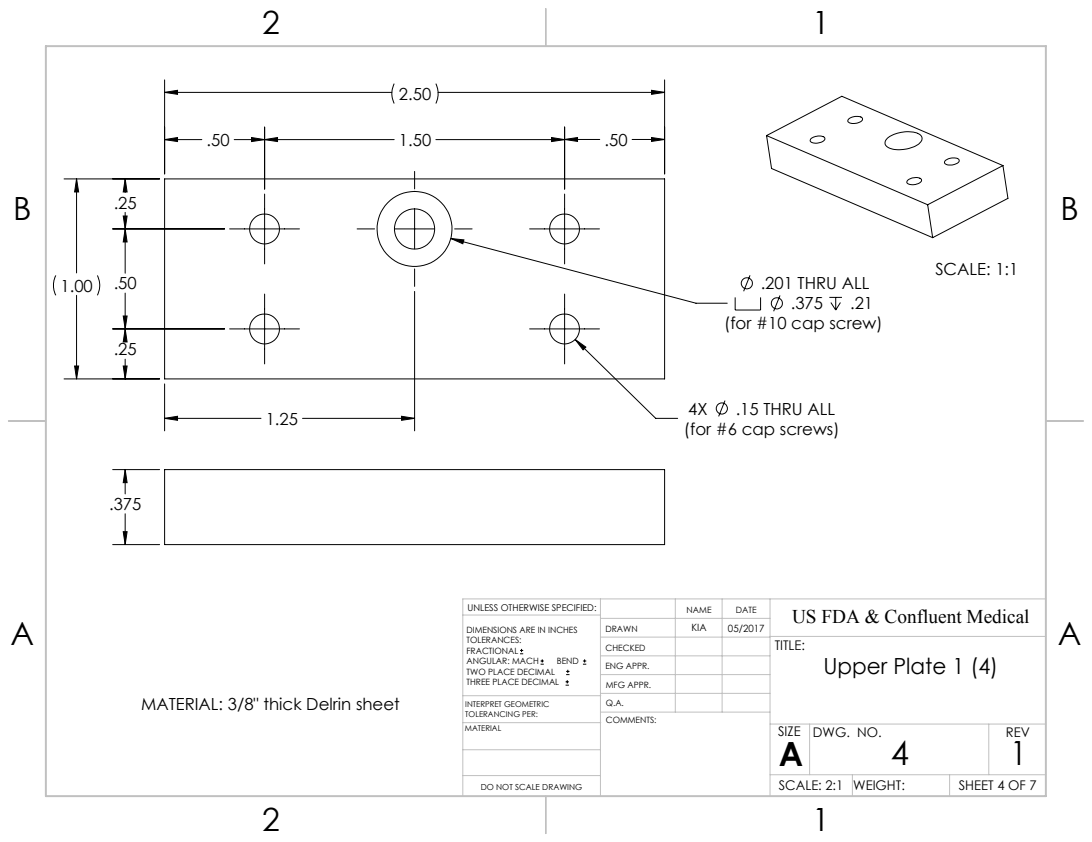
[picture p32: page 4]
.15 THRU ALL; SCALE: 1:1; SCALE: 2:1; WEIGHT:; DWG. NO.; REV

.201 THRU ALL
(for #10 cap screw)

(for #6 cap screws)

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

CHECKED | | | TITLE: Upper Plate 1 (4)

ENG APPR.
MFG APPR.

MATERIAL: 3/8" thick Delrin sheet

INTERPRET GEOMETRIC TOLERANCING PER: | Q.A.

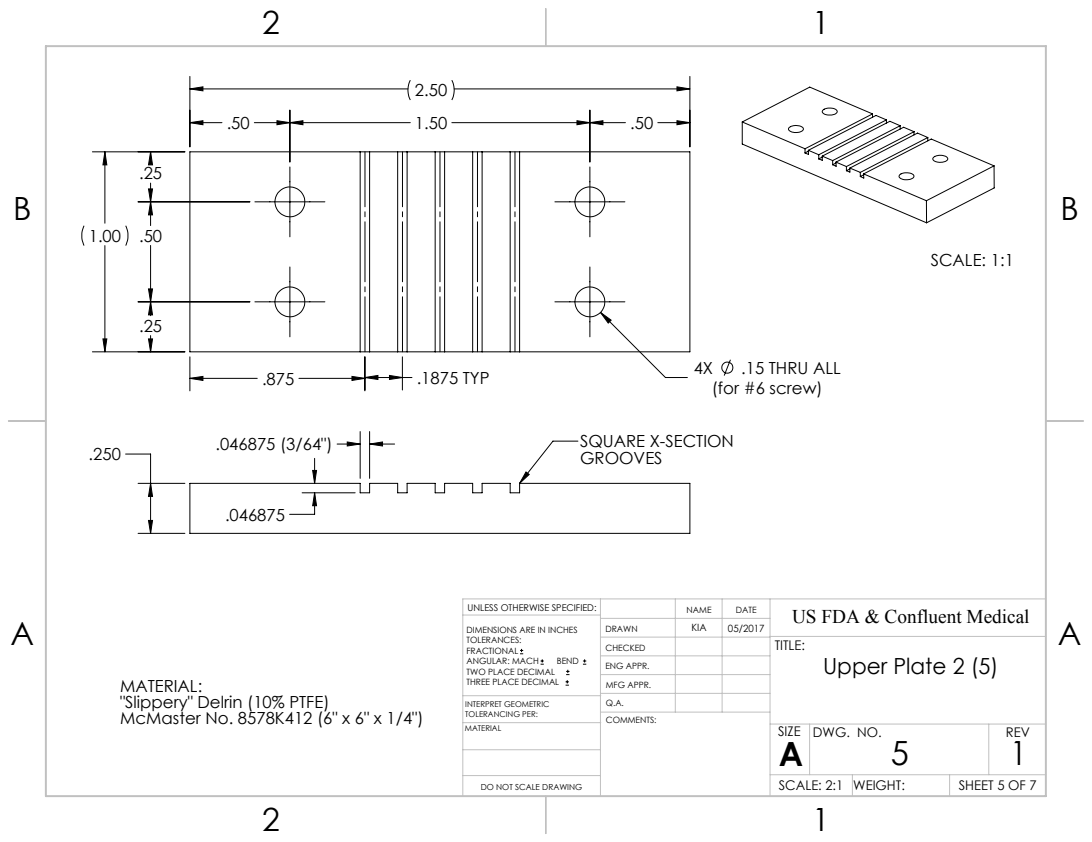
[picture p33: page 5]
.15 THRU ALL; (for #6 screw); .1875 TYP; SQUARE X-SECTION; SCALE: 1:1; DWG. NO.; REV

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

CHECKED | | | TITLE: Upper Plate 2 (5)

ENG APPR.
MFG APPR.

MATERIAL:
"Slippery" Delrin (10% PTFE)
McMaster No. 8578K412 (6" x 6" x 1/4")

INTERPRET GEOMETRIC TOLERANCING PER: | Q.A.

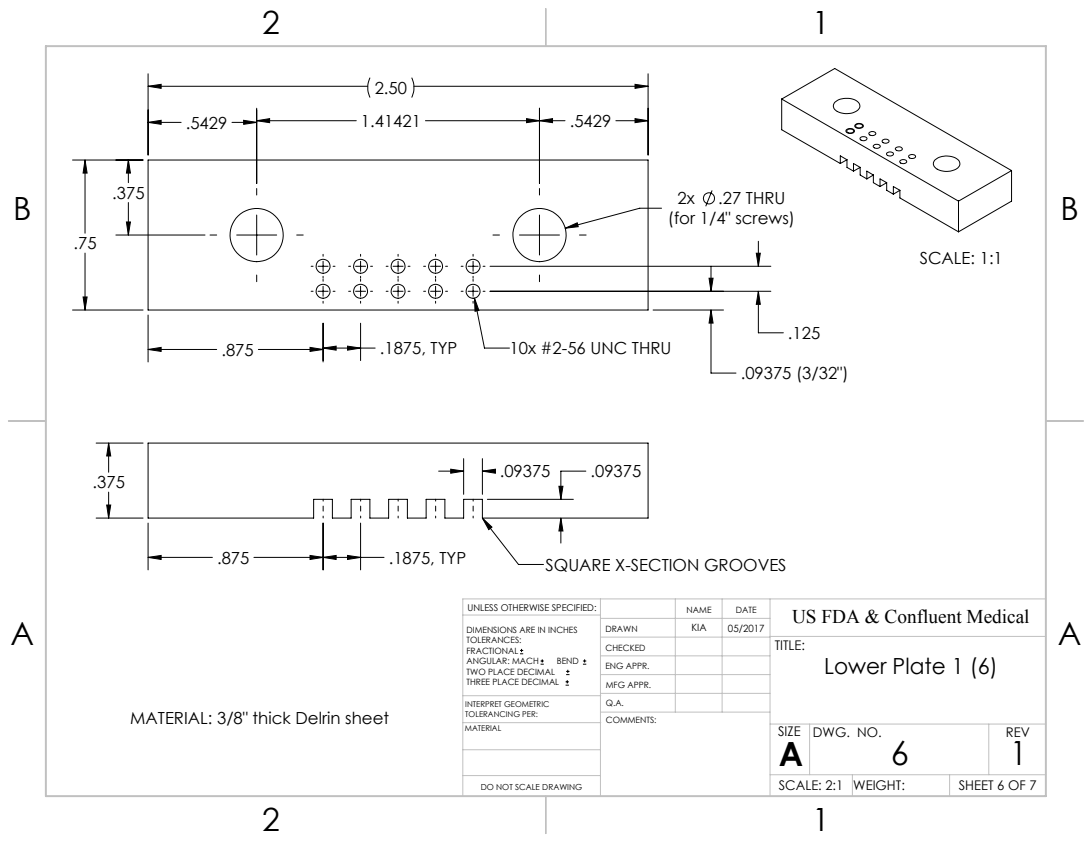
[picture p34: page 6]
SCALE: 1:1; .1875, TYP; 10x #2-56 UNC THRU; 2x .27 THRU (for 1/4" screws); SQUARE X-SECTION GROOVES; DWG. NO.; REV

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

CHECKED | | | TITLE: Lower Plate 1 (6)

ENG APPR.
MFG APPR.

INTERPRET GEOMETRIC TOLERANCING PER: | Q.A.

MATERIAL: 3/8" thick Delrin sheet

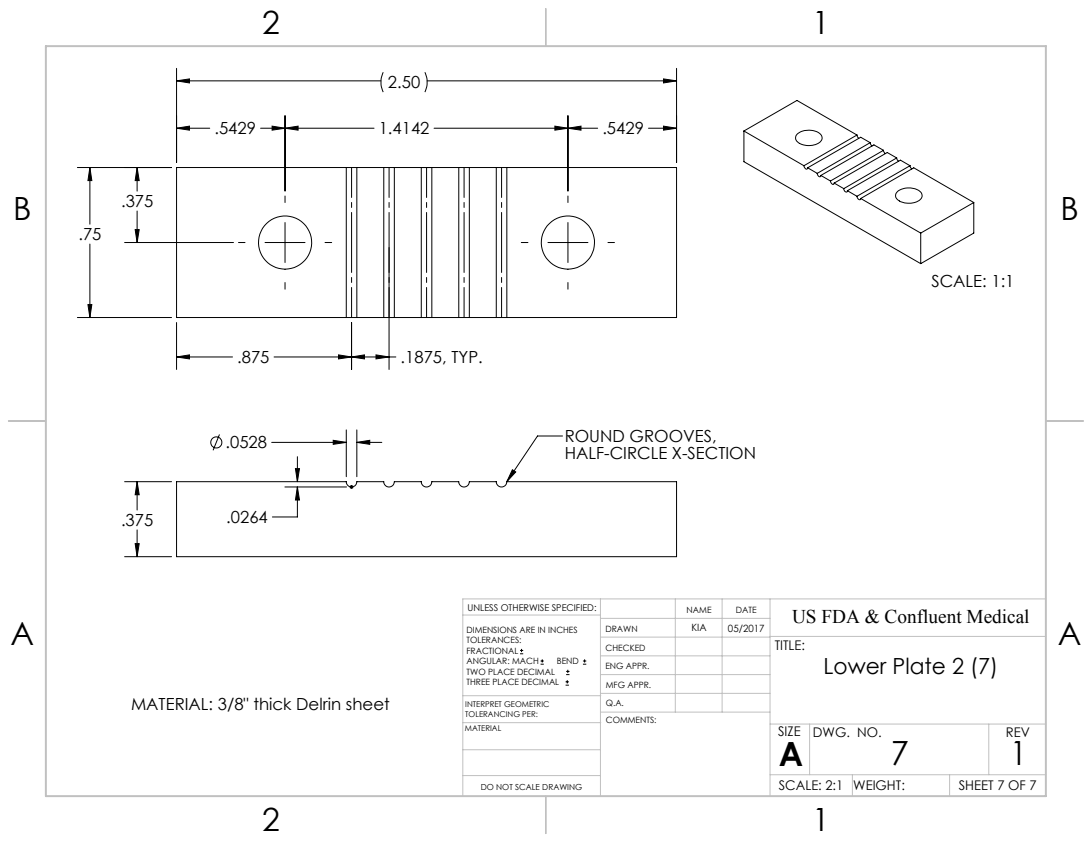
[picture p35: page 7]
SCALE: 1:1; .1875, TYP.; DWG. NO.; REV

ROUND GROOVES,
HALF-CIRCLE X-SECTION

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

CHECKED | | | TITLE: Lower Plate 2 (7)

ENG APPR.
MFG APPR.

MATERIAL: 3/8" thick Delrin sheet

INTERPRET GEOMETRIC TOLERANCING PER: | Q.A.

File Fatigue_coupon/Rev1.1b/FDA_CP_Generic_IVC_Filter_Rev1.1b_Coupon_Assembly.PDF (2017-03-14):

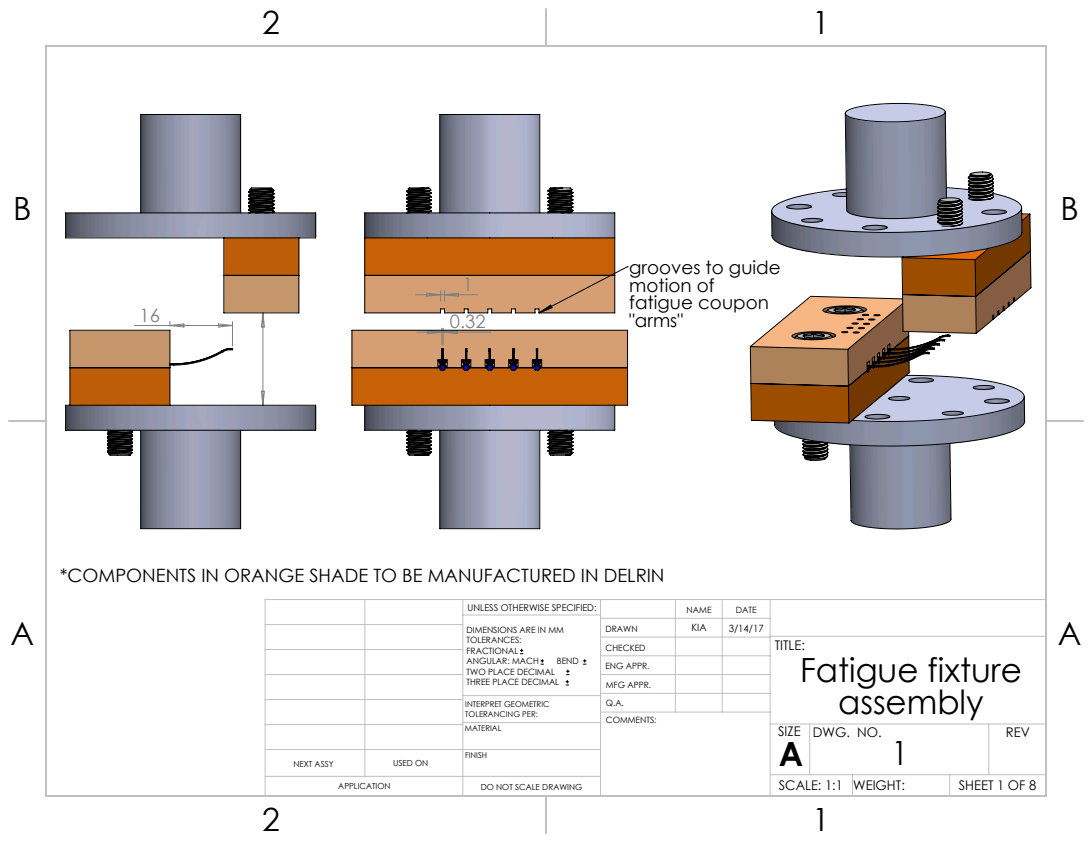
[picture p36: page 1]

grooves to guide
motion of
fatigue coupon
"arms"

*COMPONENTS IN ORANGE SHADE TO BE MANUFACTURED IN DELRIN

UNLESS OTHERWISE SPECIFIED: | | NAME | DATE
DIMENSIONS ARE IN MM TOLERANCES: FRACTIONAL ANGULAR: MACH BEND TWO PLACE DECIMAL THREE PLACE DECIMAL | DRAWN | KIA | 3/14/17

CHECKED | | | TITLE: Fatigue fixture assembly

ENG APPR.
MFG APPR.

INTERPRET GEOMETRIC TOLERANCING PER: | Q.A.
MATERIAL | | SIZE A | DWG. NO. 1 | REV

NEXT ASSY | USED ON | FINISH

APPLICATION | DO NOT SCALE DRAWING | | SCALE: 1:1 | WEIGHT: | SHEET 1 OF 8

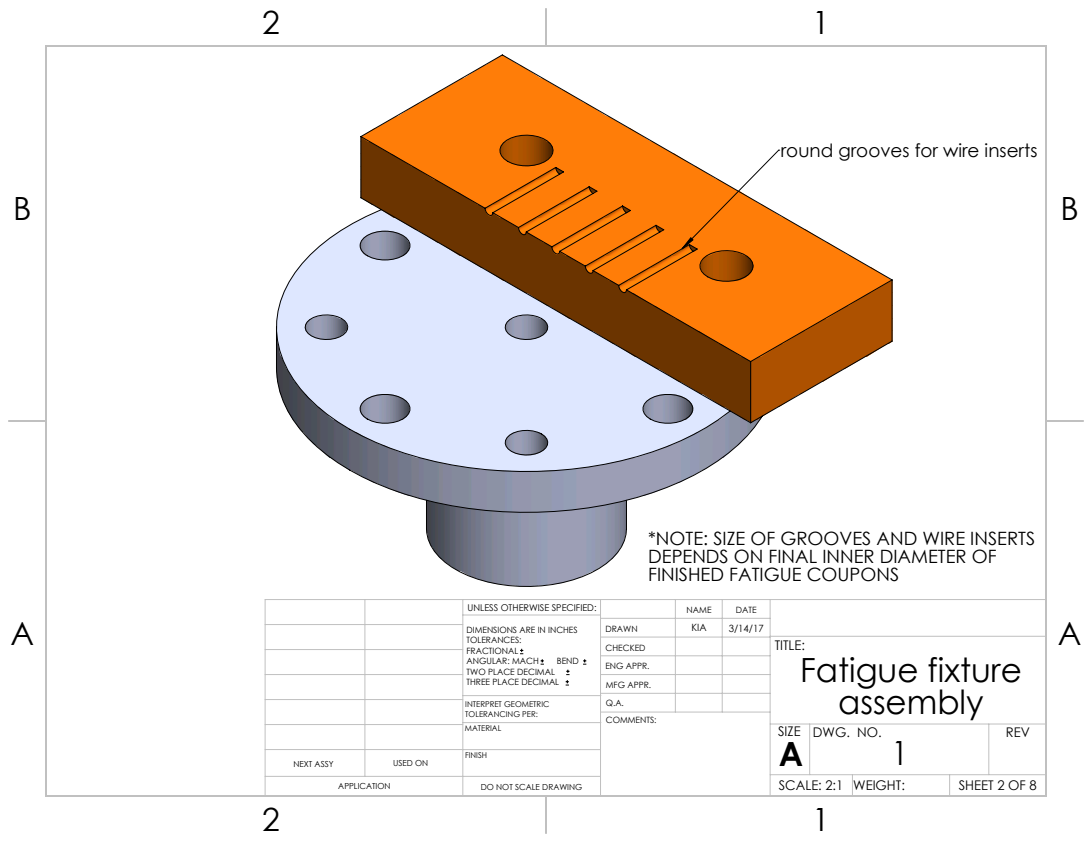
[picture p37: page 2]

round grooves for wire inserts

*NOTE: SIZE OF GROOVES AND WIRE INSERTS
DEPENDS ON FINAL INNER DIAMETER OF
FINISHED FATIGUE COUPONS

UNLESS OTHERWISE SPECIFIED: | | NAME | DATE
DIMENSIONS ARE IN INCHES TOLERANCES: FRACTIONAL ANGULAR: MACH BEND TWO PLACE DECIMAL THREE PLACE DECIMAL | DRAWN | KIA | 3/14/17

CHECKED | | | TITLE: Fatigue fixture assembly

ENG APPR.
MFG APPR.

INTERPRET GEOMETRIC TOLERANCING PER: | Q.A.
MATERIAL | | SIZE A | DWG. NO. 1 | REV

NEXT ASSY | USED ON | FINISH

SCALE: 2:1 | WEIGHT:

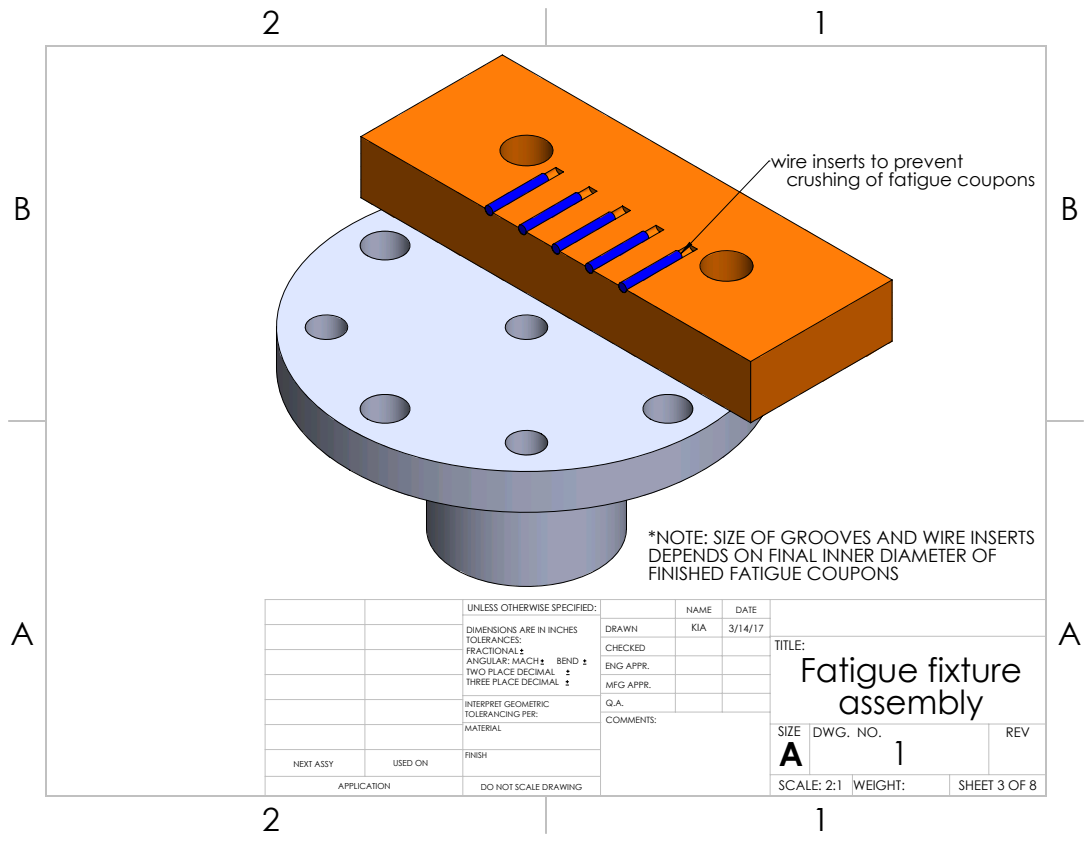
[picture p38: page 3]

wire inserts to prevent
crushing of fatigue coupons

*NOTE: SIZE OF GROOVES AND WIRE INSERTS
DEPENDS ON FINAL INNER DIAMETER OF
FINISHED FATIGUE COUPONS

UNLESS OTHERWISE SPECIFIED: | | NAME | DATE
DIMENSIONS ARE IN INCHES TOLERANCES: FRACTIONAL ANGULAR: MACH BEND TWO PLACE DECIMAL THREE PLACE DECIMAL | DRAWN | KIA | 3/14/17

CHECKED | | | TITLE: Fatigue fixture assembly

ENG APPR.
MFG APPR.

INTERPRET GEOMETRIC TOLERANCING PER: | Q.A.
MATERIAL | | SIZE A | DWG. NO. 1 | REV

NEXT ASSY | USED ON | FINISH

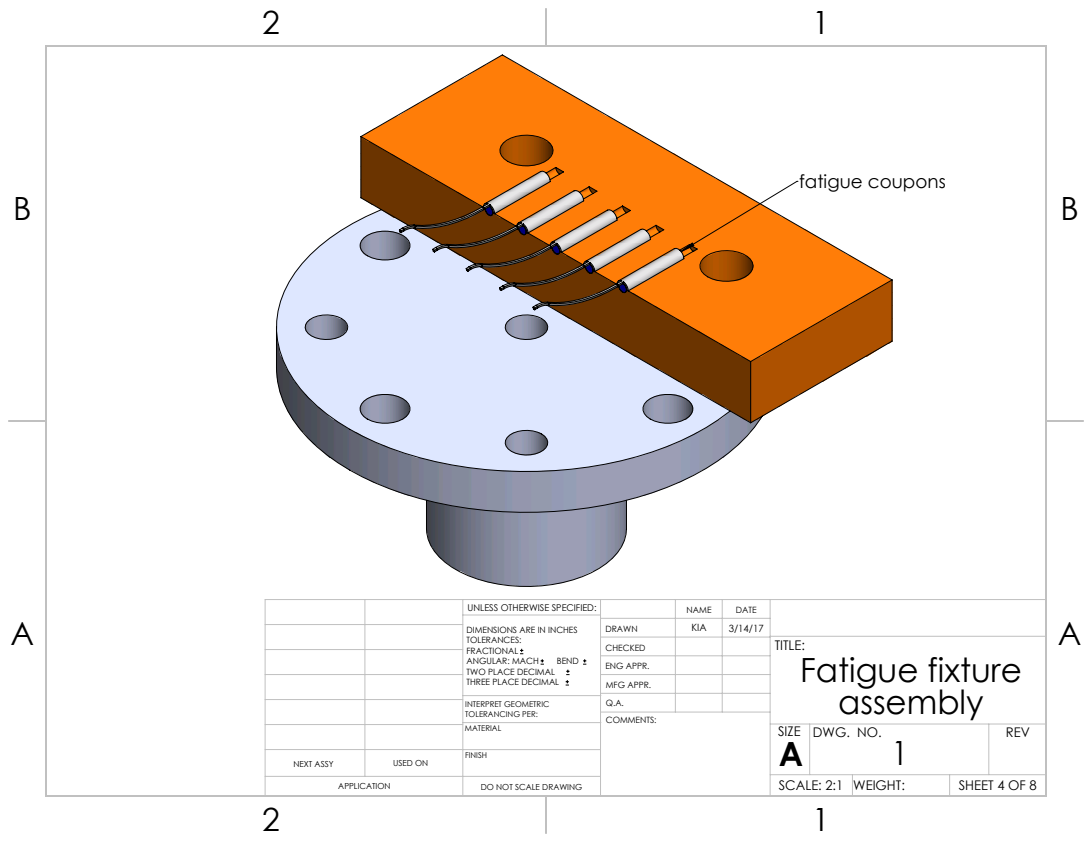
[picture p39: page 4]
fatigue coupons

UNLESS OTHERWISE SPECIFIED: | | NAME | DATE
DIMENSIONS ARE IN INCHES TOLERANCES: FRACTIONAL ANGULAR: MACH BEND TWO PLACE DECIMAL THREE PLACE DECIMAL | DRAWN | KIA | 3/14/17

CHECKED | | | TITLE: Fatigue fixture assembly

ENG APPR.
MFG APPR.

INTERPRET GEOMETRIC TOLERANCING PER: | Q.A.
MATERIAL | | SIZE A | DWG. NO. 1 | REV

NEXT ASSY | USED ON | FINISH

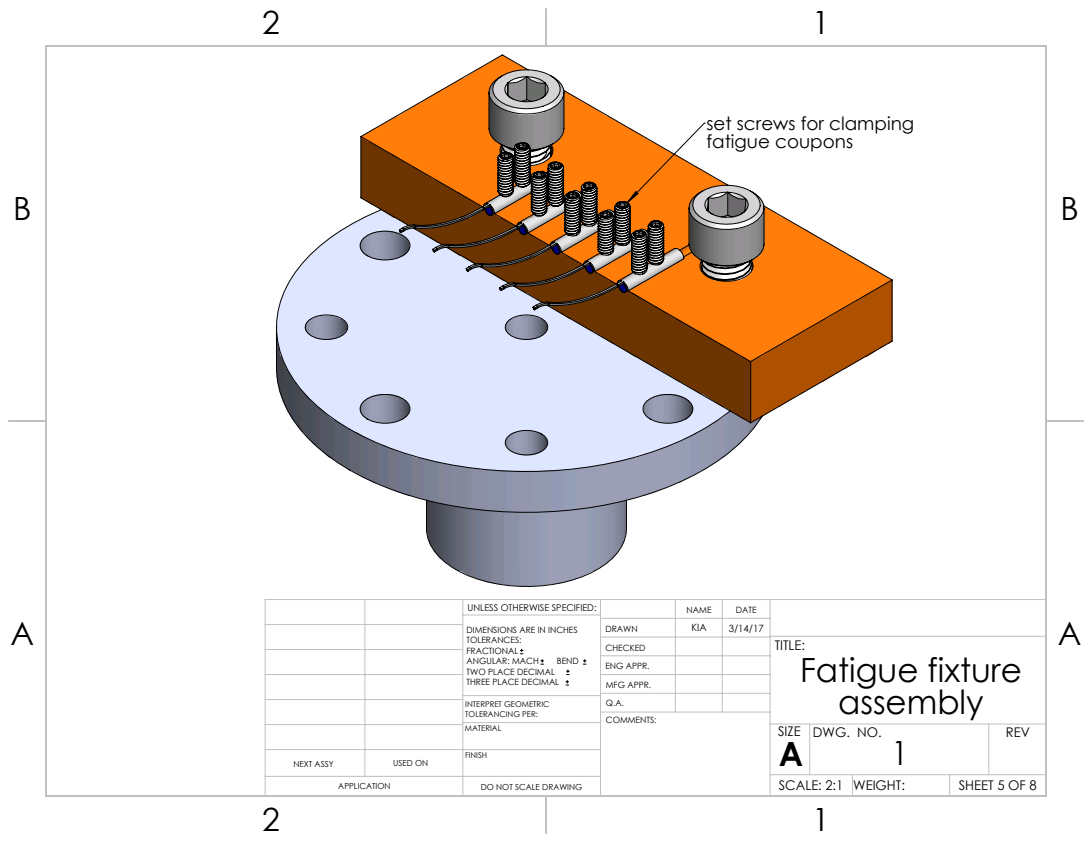
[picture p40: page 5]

set screws for clamping
fatigue coupons

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

CHECKED | | | TITLE: Fatigue fixture assembly

ENG APPR.
MFG APPR.

INTERPRET GEOMETRIC TOLERANCING PER: | Q.A.
MATERIAL | | SIZE A | DWG. NO. 1 | REV

NEXT ASSY | USED ON | FINISH

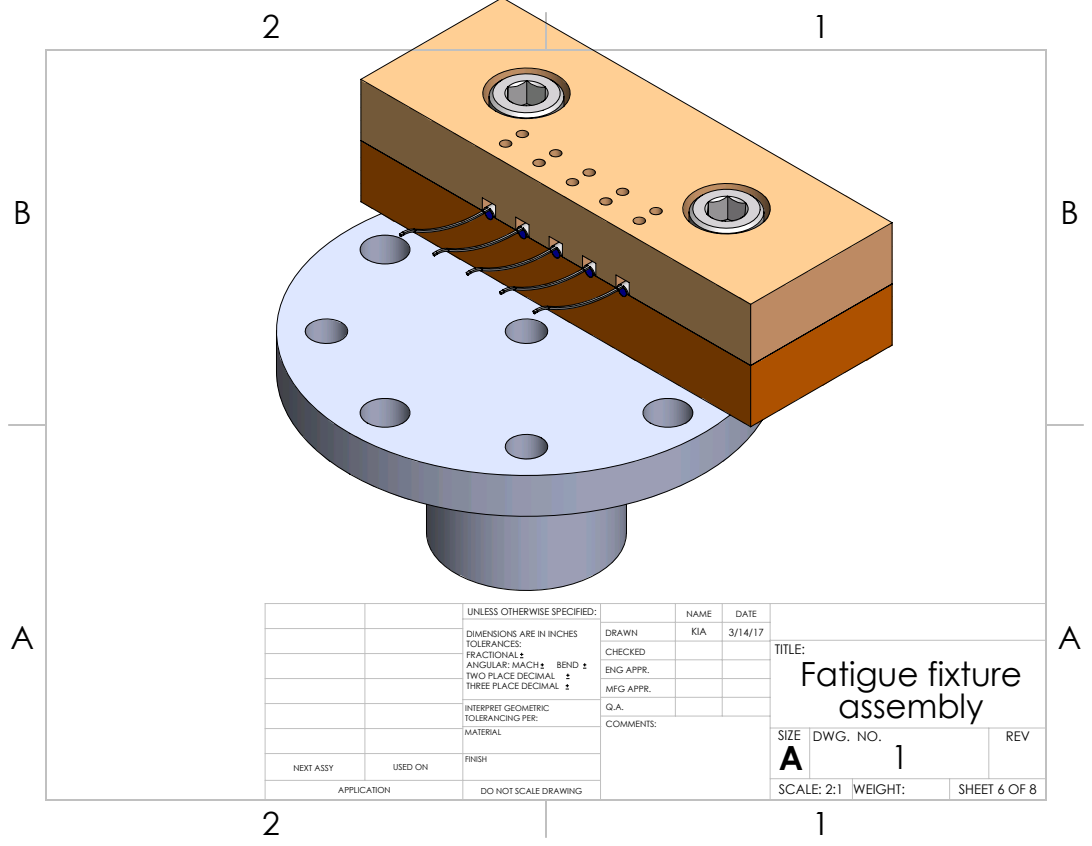
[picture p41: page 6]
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

CHECKED | | | TITLE: Fatigue fixture assembly

ENG APPR.
MFG APPR.

INTERPRET GEOMETRIC TOLERANCING PER: | Q.A.
MATERIAL | | SIZE A | DWG. NO. 1 | REV

NEXT ASSY | USED ON | FINISH

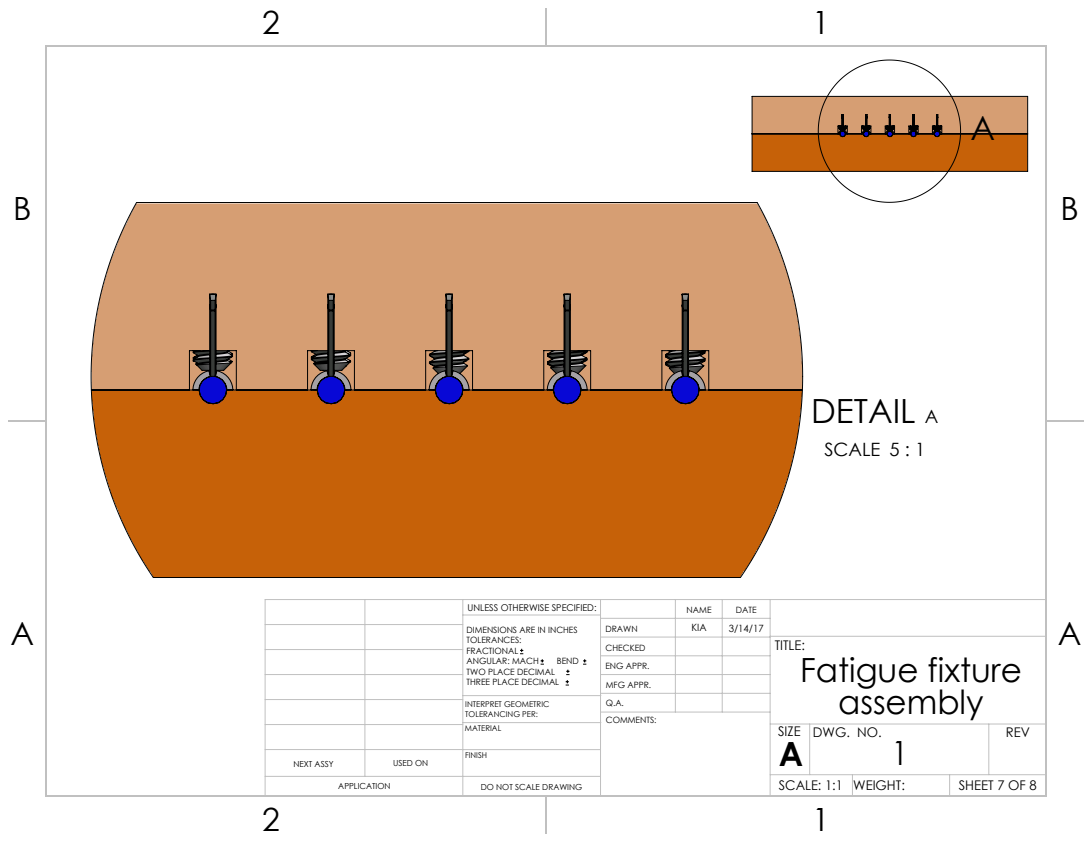
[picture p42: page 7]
DETAIL A; SCALE 5 : 1

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

CHECKED | | | TITLE: Fatigue fixture assembly

ENG APPR.
MFG APPR.

INTERPRET GEOMETRIC TOLERANCING PER: | Q.A.
MATERIAL | | SIZE A | DWG. NO. 1 | REV

NEXT ASSY | USED ON | FINISH

SCALE: 1:1 | WEIGHT:

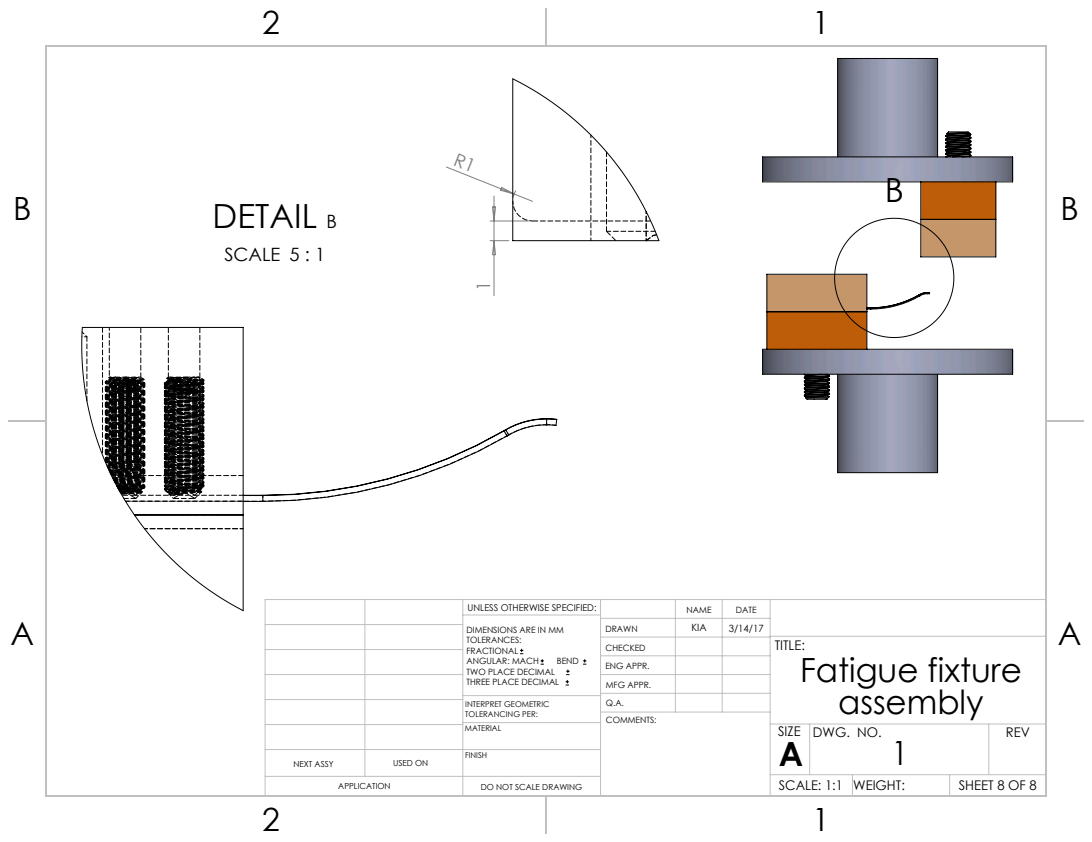
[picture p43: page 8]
DETAIL B; SCALE 5 : 1

UNLESS OTHERWISE SPECIFIED: | | NAME | DATE
DIMENSIONS ARE IN MM TOLERANCES: FRACTIONAL ANGULAR: MACH BEND TWO PLACE DECIMAL THREE PLACE DECIMAL | DRAWN | KIA | 3/14/17

CHECKED | | | TITLE: Fatigue fixture assembly

ENG APPR.
MFG APPR.

INTERPRET GEOMETRIC TOLERANCING PER: | Q.A.
MATERIAL | | SIZE A | DWG. NO. 1 | REV

NEXT ASSY | USED ON | FINISH

SCALE: 1:1 | WEIGHT:

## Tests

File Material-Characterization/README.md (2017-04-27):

# Material Characterization

UMAT material constants:

| Parameter | Value | 
|:-------------:|:-------------:| 
| E<sub>a</sub> | 59,000 MPa |
| 𝜈<sub>a</sub> | 0.33 |
| E<sub>m</sub> | 24,750 MPa |
| 𝜈<sub>m</sub> | 0.33 | 
| ε<sup>L</sup> | 0.042 |
| 𝛿σ/𝛿T<sub>L</sub> | 4.77 MPa / °C |
| σ<sup>S</sup><sub>L</sub> | 395 MPa |
| σ<sup>E</sup><sub>L</sub> | 435 MPa |
| T<sub>0</sub> | 37 °C |
| 𝛿σ/𝛿T<sub>U</sub> | 9.00 MPa / °C |
| σ<sup>S</sup><sub>U</sub> | 165 MPa |
| σ<sup>E</sup><sub>U</sub> | 145 MPa |
| σ<sup>S</sup><sub>cL</sub> | ~~395~~ <sup>*</sup>513.5 MPa |
| ε<sup>L</sup><sub>V</sub> | 0.042 | 
| N<sub>A</sub> | 0 |
| N<sub>P</sub> | 3 |
| σ<sup>P</sup><sub>1</sub> | 1205 MPa |
| ε<sup>P</sup><sub>1</sub> | 0.090 |
| σ<sup>P</sup><sub>2</sub> | 1350 MPa |
| ε<sup>P</sup><sub>2</sub> | 0.100 |
| σ<sup>P</sup><sub>3</sub> | 1450 MPa | 
| ε<sup>P</sup><sub>3</sub> | 0.120 |

<sup>*</sup> Scaling ratio of σ<sup>S</sup><sub>cL</sub> = 1.30 σ<sup>S</sup><sub>L</sub>; see '[Material characterization](https://github.com/kenaycock/Generic-IVC-Filter/issues/5)' issue.

Plot of experimental data and ABAQUS UMAT with above constants:
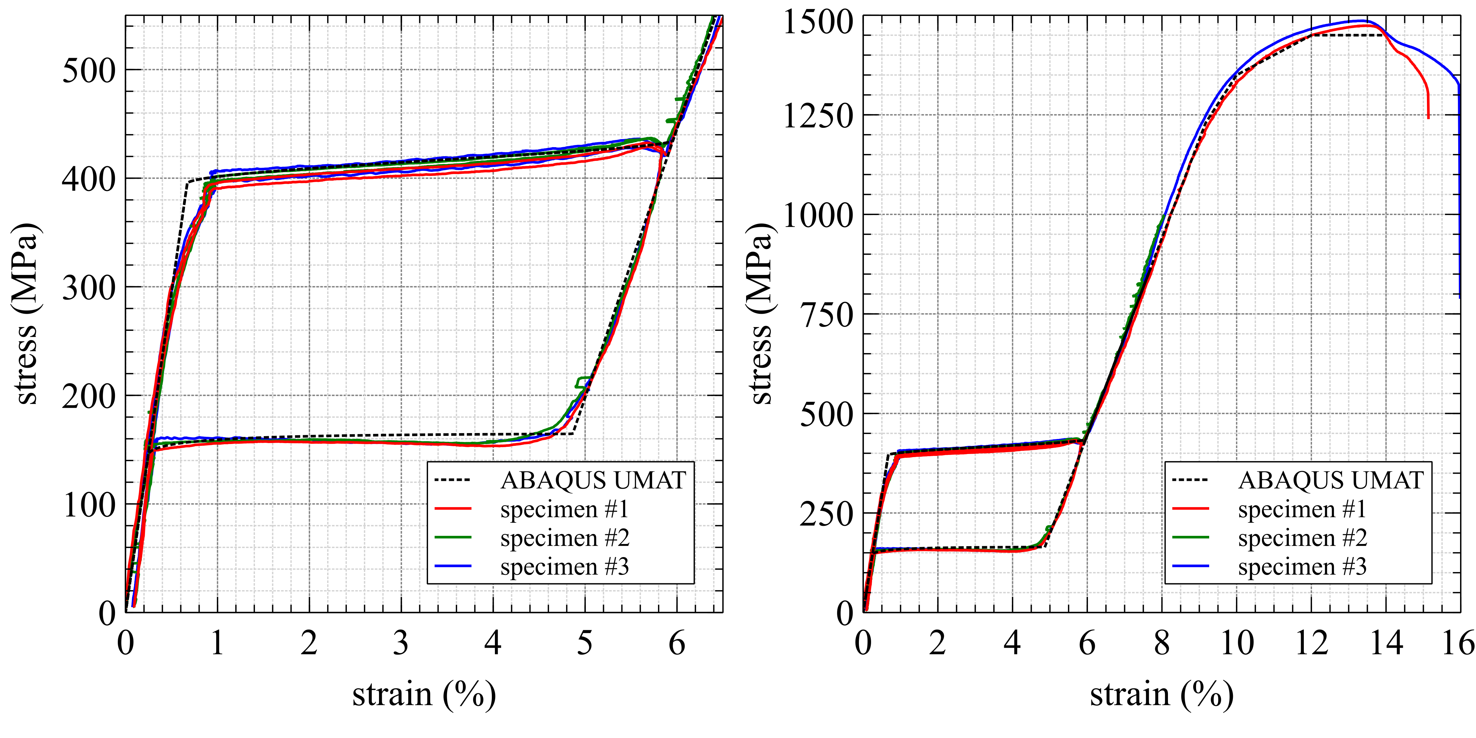
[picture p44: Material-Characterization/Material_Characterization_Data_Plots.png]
stress-strain_plot_37C_low_strain


The nitinol UMAT verification was performed using a single C3D8R element (one integration point). The logarithmic strain (LE22, or ε<sub>yy</sub>) and the Cauchy stress (S22, or σ<sub>yy</sub>) were extracted from the ODB simulations result file.

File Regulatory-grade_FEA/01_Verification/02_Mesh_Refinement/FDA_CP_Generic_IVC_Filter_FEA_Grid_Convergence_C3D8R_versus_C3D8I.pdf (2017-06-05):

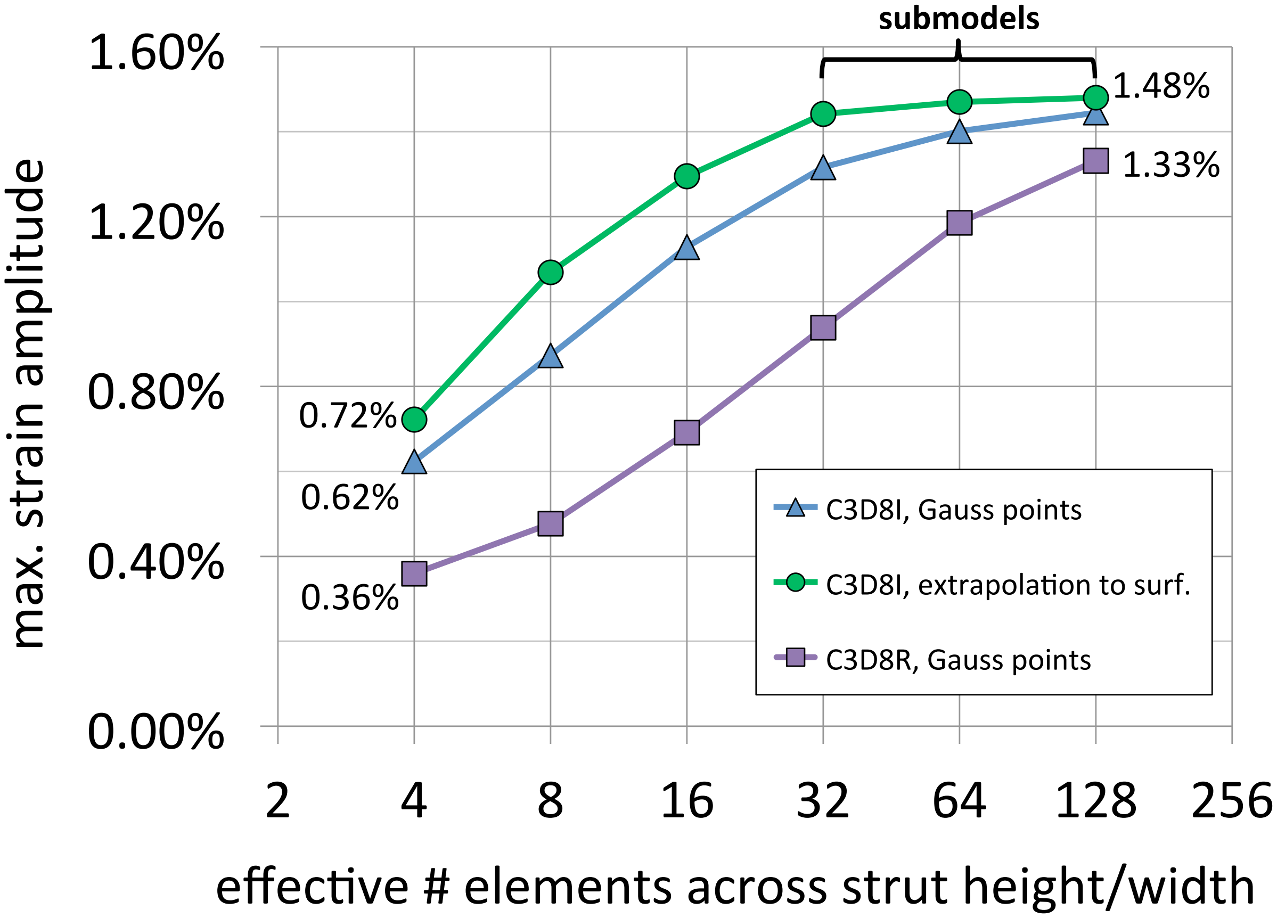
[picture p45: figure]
max. strain amplitude; C3D8R, Gauss points; submodels

0.62% 0.36% | C3D8I, Gauss points C3D8I, extrapola<on to surf.

effec<ve # elements across strut height/width

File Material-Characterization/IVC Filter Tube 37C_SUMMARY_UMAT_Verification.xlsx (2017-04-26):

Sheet: Summary_37C
true_strain_1 | true_stress_1 | true_strain_2 | true_stress_2 | true_strain_3 | true_stress_3 | abaqus_strain_LE22 | abaqus_stress_S22
-0.001730015 | 4.935674611 | 0.006939759193 | 5.129245945 | 0.000399999 | 5.078110312 | 0 | 0
0.008289656 | 14.28179386 | 0.01693856534 | 12.0433798 | 0.010419457 | 12.97503186 | 0.00799968 | 4.71981
0.018308324 | 23.7241431 | 0.02694636914 | 22.25804693 | 0.020457907 | 15.3002998 | 0.0159987 | 9.43925 | ABAQUS UMAT constants:
0.028325988 | 33.03281555 | 0.03699315669 | 28.40656654 | 0.030465359 | 22.6491591 | 0.0239971 | 14.1583 | E_a | 59000 | MPa
0.038332652 | 43.3692614 | 0.04705892555 | 34.61575597 | 0.040521789 | 29.07118778 | 0.0319949 | 18.877 | nu_a | 0.33
0.048338315 | 48.5543847 | 0.05706371556 | 40.10000603 | 0.050547223 | 35.30525131 | 0.039992 | 23.5953 | E_m | 24750 | MPa
0.058342977 | 53.32554264 | 0.06714745105 | 47.76509228 | 0.060581646 | 43.00386456 | 0.0479885 | 28.3132 | nu_m | 0.33
0.068356632 | 60.62781897 | 0.07715023155 | 52.31782776 | 0.070615062 | 48.59137071 | 0.0559843 | 33.0308 | e_l | 0.042
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

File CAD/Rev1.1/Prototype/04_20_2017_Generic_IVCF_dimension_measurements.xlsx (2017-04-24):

 | FDA IVC Filter
 | Lot 2095742
 | Strut Width (in) | Wall Thickness (in)
Leg 1 | 0.01318 | 0.01334
 | 0.01314 | 0.01339
Leg 3 | 0.01311 | 0.01374
 | 0.01308 | 0.01383
Leg 5 | 0.01305 | 0.01271
 | 0.01308 | 0.01295
Leg 7 | 0.01314 | 0.01428
 | 0.01315 | 0.01399
Leg 9 | 0.01318 | 0.01415
 | 0.01317 | 0.01409
Leg 11 | 0.01321 | 0.01354
 | 0.01311 | 0.01311
Leg 13 | 0.01321 | 0.01395
 | 0.01328 | 0.01378
Leg 15 | 0.01324 | 0.01370
 | 0.01323 | 0.01336
Min. (mm) | 0.3315 | 0.3228
Max. (mm) | 0.3373 | 0.3627
Average (mm) | 0.3343 | 0.3459
St. Dev. (mm) | 0.0016 | 0.0114

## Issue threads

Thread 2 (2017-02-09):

### ISSUE TITLE
Rev1.1 CAD Design of Generic IVC filter

### ISSUE THREAD

**Issue by kenaycock** [kenaycock/Generic-IVC-Filter#2]
Hi Karthik, 

I uploaded new CAD files for the generic IVC filter along with a DXF file for the laser cutting:
https://github.com/kenaycock/Generic-IVC-Filter/tree/master/CAD/Rev1.1
Could you take a look at the updated files and see if we need to make further changes before proceeding with manufacturing a prototype? 

I assumed the following values in the CAD model based on those given in the *Open Stent* manuscript:
* Laser kerf width ("w_kerf"): 0.025mm
* Material removed during surface finishing:
    * "m_width": 0.036mm (i.e., 0.018mm from each side of the struts)
    * "m_thickness": 0.059mm (from the *inside* surface of the tube to remove draw lines)

Are these values appropriate for 1) this size of tubing and 2) our chosen surface finishing? I believe we decided on electropolishing during our last meeting.

I think specifying an accurate kerf width is all that really matters right now, but we will eventually need to know the material removed during surface finishing so that we can perform accurate FEA simulations using the "finished" device geometry. 

Anyway, I look forward to your feedback! 

Thanks,
Kenny

**Comment by karthikSenthi** [comment]
Hi Kenny,

I reviewed the CAD files and it all looks good. For the material removal due to surface finishing, you can assume the total removal from the strut width to be 0.025mm (i.e 0.0125mm from each side). For the wall thickness, it is better to specify the value and tolerances after measuring dimensions from initial prototypes. For now, just the initial starting thickness of the tube in the drawing should suffice. 

Please update the laser kerf width accounting for this new removal and upload the relevant files. Also for the dxf file, it seems you uploaded the coding for a tool path which we don't need. Instead, if you could save the "Laser Toolpath DXF" sheet of the SolidWorks drawing you created in a separate dxf/dwg file that should be good.

Thanks,
Karthik

**Comment by kenaycock** [comment]
Hi Karthik,

Okay, sounds good. The "as-cut" configurations that I uploaded are based on
a total laser kerf of 0.025mm as you said (0.0125mm per side), so I think
we are set. I can update the "finished" configurations after we make a
prototype. But, I can add an "as-cut, expanded" drawing if
you need that.

Regarding the DXF file, did you open this on your workstation, or did you
preview the file on GitHub? Since the file is ASCII, GitHub shows you the
raw code as if it were a toolpath or something, but if you open the file in
a DXF viewer it should load normally. Let me know if there's something
wrong though and I can re-export the drawing.

EDIT: Here's a direct link to the DXF file that you can save out from your browser using "File->Save as...":
https://raw.githubusercontent.com/kenaycock/Generic-IVC-Filter/master/CAD/Rev1.1/FDA_CP_Generic_IVC_Filter_Rev1.1_Laser_template.DXF

Thanks,
Kenny

**Comment by karthikSenthi** [comment]
Hi Kenny,

Just to clarify, I meant "m_width" to be 0.025mm (i.e the material removal from strut width) and not kerf_width. So the kerf_width will be higher than 0.025mm if you adjust the as-cut dimension accordingly.

I am able to view the dxf file after saving it to the computer. If you could upload the revised files then we should be good to produce the prototypes.

-Karthik

**Comment by kenaycock** [comment]
Hi Karthik, 

Thanks for the clarification. I misunderstood your first message. I can update "m_width" to 0.025mm (currently 0.036mm) as you directed. A couple more questions to clear this up: 

1. Should the laser kerf width also be 0.025mm, as I previously specified?
2. Should the "as cut" configuration include the laser kerf only and be independent of "m_width"?

Regarding (2), I'm slightly confused. In the _Open Stent_ manuscript, the "as cut" width is defined as:

> w_strut_raw = (D_tube * pi / N_struts) - w_kerf (Eqn. 3.38)

where:
> "w_kerf is the effective kerf width between struts when fabricated (or in the crimped state). In the typical case of laser micromachining of stent from tubing, this is the effective width of the laser beam:
w_kerf = 0.025mm   (Eqn. 3.11)"

The "as cut" configurations that I provided in the drawings thus far follow the procedure in the _Open Stent_ manuscript and account for the laser kerf only. But, it sounds like maybe you're asking for something else?

Feel free to give me a call you'd like to discuss.

Kenny

**Comment by karthikSenthi** [comment]
Hi Kenny,

To answer your questions,

- The 0.025mm for kerf width is a general guidance. The laser kerf width can be more than that depending on your final dimensions that you are trying to achieve. You can calculate the required kerf width based on Eqn 3.38 since you know your w_strut_raw ( w_strut_raw= targeted_finished_w_strut+m_width). If you are fine with a higher finished w_strut then you can assume both the w_kerf and m_width to be 0.025mm.

-  The as cut configuration should be independent of the "m_width" as "m_width" corresponds to the material removal that you expect from surface processing.

Karthik

**Comment by kenaycock** [comment]
Hi Karthik,

"If you are fine with a higher finished w_strut then you can assume both
the w_kerf and m_width to be 0.025mm."

Ah, I see. My aim was to make the struts as wide as possible, so
w_kerf=m_width=0.025mm is fine.

With this information, is the DXF file suitable as-is? I will correct the
"m_width" value tonight.

Kenny

**Comment by karthikSenthi** [comment]
If that's the case the DXF should be good.

**Comment by kenaycock** [comment]
Okay, thanks, Karthik. Sorry for the mixup. I didn't realize that you would
be treating the "finished" drawings as target dimensions, but that makes
sense.

Now that I think about it some more, it probably would not be a bad idea to
make the gap between the struts a *little* wider to make sure we do not
have too much strut-strut interference during sheathing, etc.

What is the range of kerf width that you can achieve with the laser in a
single pass? Would 0.050mm be acceptable?

**Comment by karthikSenthi** [comment]
Sure it can be more than 0.025mm for the kerf_width and we can do a multi-pass cut to get to 0.050 mm kerf width. If it is wider, it will be easier and more uniform for the laser cutting to get the targeted kerf_width at the laser entry and exit point.

**Comment by kenaycock** [comment]
I uploaded new files with:
* w_kerf = 0.050mm
* m_width = 0.025mm

This gives us a total gap between struts of 0.075mm in the "finished" configuration, which is close to what we had in the "Rev1" CAD model that I analyzed with FEA (0.1mm).

Can you take a look at the files one more time? I think we are close now.

**Comment by karthikSenthi** [comment]
Hi Kenny,

It looks all good now. Nice job.

Thanks,
Karthik

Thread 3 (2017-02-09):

### ISSUE TITLE
Add Af spec to drawing

### ISSUE THREAD

**Issue by cbonsig** [kenaycock/Generic-IVC-Filter#3]
The target Af should be added to the drawing. Ideally, specify something like Af 25 +/-5 C by bend bree recovery method.

**Comment by kenaycock** [comment]
Hi Craig, 

I updated the drawing files as requested:
https://github.com/kenaycock/Generic-IVC-Filter/tree/master/CAD/Rev1.1

I'm looking at Figure 3.3 in the OpenStent manuscript and it appears that an A<sub>f</sub> of 25 °C corresponds to an Austenite elastic modulus of E<sub>A</sub> ≈ 45,000 MPa:
![openstent_manuscript_fig_3 3](https://cloud.githubusercontent.com/assets/5925722/22793817/fcb5987e-eebe-11e6-93ed-529aad0b1eae.png)



However, I performed our preliminary FEA analyses using E<sub>A</sub> = 61,779 MPa
(same constants as in https://github.com/cbonsig/strain-amplitude-volume-fraction/blob/master/Abaqus_6.12-1_Example.inp). If I'm understanding this correctly, then our prototypes will be ≈3/4 as stiff as the computer model for small strains? That's probably fine, but it would be good to know in advance.

Thanks!
Kenny

**Comment by cbonsig** [comment]
I wouldn't use the Open Stent figure as a general reference for Ea vs Af. That chart was intended to show that there is a relationship that can be modeled, but the specifics will depend on the material history. When we do material testing for this component, we will test at two temperatures, and that will give us the Ea vs Af relationship for this material and process. (Ea and the plateau stresses will shift with the difference between Af and environmental temperature -- so the effect of dropping Af by 10 degrees is equivalent to the effect of raising the environment temperature by 10 degrees while holding Af constant -- that's how we can measure the effect of changing Af without actually making components with a different Af)

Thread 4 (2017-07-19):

### ISSUE TITLE
Proposed fatigue coupon and fatigue fixture designs

### ISSUE THREAD

**Issue by kenaycock** [kenaycock/Generic-IVC-Filter#4]
Hi Karthik and Craig,

We recently revised the design of the generic IVC filter fatigue coupons and also drafted a design for the fatigue fixture. Summary drawings of the proposed designs can be found here:
https://github.com/kenaycock/Generic-IVC-Filter/tree/master/Fatigue_coupon/Rev1.1b

The proposed fatigue coupon is similar to the one we discussed earlier, but:
1. we extended the hub length to 1cm so that the gripping stresses are located farther from the coupon "arm", and 
2. we removed half of the coupon hub so that the coupon is easier to align and clamp. These "half-tube" coupons should also conserve material, since two fatigue coupons can now be cut from the same length of tubing as would be needed for a single coupon with our earlier design.  

Could you take a look and let us know if you have any feedback? In particular, do you anticipate any problems manufacturing these "half-tube" coupons?

Thanks!
Kenny

**Comment by cbonsig** [comment]
Manufacturing should be straightforward, and the test assembly looks reasonable. I suspect that the cyclic strains may be quite low, so if the intent is to test to failure, that might be a challenge with this setup.

**Comment by cbonsig** [comment]
Another thought. We know from the preliminary analysis (https://github.com/kenaycock/Generic-IVC-Filter/blob/master/Preliminary_FEA/Generic_IVC_filter_project_Preliminary_FEA_Summary.pdf) that 1mm deflection achieves about 0.1% strain amplitude. Higher strain amplitudes can be achieved by deflecting the strut down to the hub diameter, or possibly below the hub diameter... However, with the flat plate test fixture, as the deflection approaches a limit somewhere near the hub diameter, the point of contact will change from the tip of the strut to a point closer to the hub. If such extreme deflections prove to me necessary, it may be helpful to change the design of the top plate to reduce its width and ensure that the point of contact remains at the tip of the strut.

**Comment by kenaycock** [comment]
Hi Craig,

I reviewed our earlier FEA simulations that we performed with the current
coupon design and it looks like deflecting the strut down to the hub
diameter only produces a maximum strain amplitude of approximately 0.5% and
requires a vertical stroke displacement of ≈5mm. Deflecting the tip of the
strut *beyond* the hub diameter another ≈5 mm or so will generate a maximum
strain amplitude of approximately 1% (and require a stroke of ≈10mm). So,
we might be able to make the current design work, but it's probably not
ideal for testing to failure.

Yesterday you mentioned the possibility of producing multiple coupon shapes
or sizes. If it's not too much trouble, what would you think of using the
current coupon design (Rev1.1b) to characterize the lower strain amplitudes
(from 0.1% to 0.5%) and a second coupon with a shorter strut length and a
larger angle between the strut and the axis of the hub to characterize the
larger strain amplitudes (from 0.5% up to, say, 1.5%)?

The problem with using a short coupon for the full range of strain
amplitudes we are interested in (from 0.1% to 1.5%) is that, for the small
strain amplitudes like that corresponding to the Valsalva case for the full
device (0.1%), the required displacements are quite small. For example,
based on some analysis I just ran, for a 6mm strut length, 1.5% strain
amplitude corresponds to a stroke displacement of 1.2mm (reasonable), but
0.1% strain amplitude corresponds to a total stroke displacement of only
≈0.1mm. I imagine consistently producing displacements that small over
multiple coupon specimens may be challenging.

Also, I think you are right that we should reduce the width of the top
plate or reposition it so that the contact point remains approximately the
same throughout the fatigue cycle. If we do pursue multiple coupon designs,
we'll need to adjust the design of the top plate accordingly (perhaps by
adding slots to make the plate mounting position variable).

On Mar 22, 2017 23:08, "Craig Bonsignore" <notifications@github.com> wrote:

Another thought. We know from the preliminary analysis (
https://github.com/kenaycock/Generic-IVC-Filter/blob/master
/Preliminary_FEA/Generic_IVC_filter_project_Preliminary_FEA_Summary.pdf)
that 1mm deflection achieves about 0.1% strain amplitude. Higher strain
amplitudes can be achieved by deflecting the strut down to the hub
diameter, or possibly below the hub diameter... However, with the flat
plate test fixture, as the deflection approaches a limit somewhere near the
hub diameter, the point of contact will change from the tip of the strut to
a point closer to the hub. If such extreme deflections prove to me
necessary, it may be helpful to change the design of the top plate to
reduce its width and ensure that the point of contact remains at the tip of
the strut.

—
You are receiving this because you authored the thread.
Reply to this email directly, view it on GitHub
<https://github.com/kenaycock/Generic-IVC-Filter/issues/4#issuecomment-288604717>,
or mute the thread

**Comment by kenaycock** [comment]
Hi Craig,

I reviewed our earlier FEA simulations that we performed with the current coupon design and it looks like deflecting the strut down to the hub diameter only produces a maximum strain amplitude of approximately 0.5% and requires a total cyclic vertical displacement of ≈3mm (1.5mm displacement amplitude). Deflecting the tip of the strut *beyond* the hub diameter another ≈3 mm, we can generate a maximum strain amplitude of approximately 1.5%. So, we might be able to make the current design work, but it's probably not ideal for testing to failure.
![fatigeu_coupon_Rev1.1b_max_strain_amp_1pt5perc](https://cloud.githubusercontent.com/assets/5925722/24262639/156c0564-0fd1-11e7-8e0a-97d3bf7ae8c0.gif)
***Animation:** Fatigue loading of the "Rev1.1b" coupon, with a total cyclic displacement of the distal end of the strut of 6mm, corresponding to a strain amplitude of approximately 1.5%* 

Yesterday you mentioned the possibility of producing multiple coupon shapes or sizes. If it's not too much trouble, what would you think of using the current coupon design (Rev1.1b) to characterize the lower strain amplitudes (from 0.1% to 0.5%) and a second coupon with a shorter strut length and a larger angle between the strut and the axis of the hub to characterize the larger strain amplitudes (from 0.5% up to, say, 1.5%)?

The problem with using a short coupon for the full range of strain amplitudes we are interested in (from 0.1% to 1.5%) is that, for the small strain amplitudes like that corresponding to the Valsalva case for the full device (0.1%), the required displacements are quite small. For example, based on some analysis I just ran, for a 6mm strut length, 1.5% strain amplitude corresponds to a stroke displacement of 1.2mm (reasonable), but 0.1% strain amplitude corresponds to a total stroke displacement of only ≈0.1mm. I imagine consistently producing displacements that small over multiple coupon specimens may be challenging.

Also, I think you are right that we should reduce the width of the top plate or reposition it so that the contact point remains approximately the same throughout the fatigue cycle. If we do pursue multiple coupon designs, we'll need to adjust the design of the top plate accordingly (perhaps by adding slots to make the plate mounting position variable).

**Comment by cbonsig** [comment]
I think that a second shorter coupon is a good idea. At 1.5% strain, we should be able to get to a condition with high fracture probability in a reasonable number of cycles.

**Comment by kenaycock** [comment]
@cbonsig  @karthikSenthi
Hi Craig, Karthik:

As communicated via e-mail, we recently finished revising our fatigue coupons. I'm uploading the same slide deck that I sent out earlier here for public.

The updated design files can be found here: 
https://github.com/kenaycock/Generic-IVC-Filter/tree/master/Fatigue_coupon/Rev1.2

[05_15_2017_Fatigue_coupons_update.pdf](https://github.com/kenaycock/Generic-IVC-Filter/files/1002437/05_15_2017_Fatigue_coupons_update.pdf)

Let us know if you have any feedback. We plan on testing 10 specimens per condition (so ~50 "high-strain" and ~30 "low-strain" coupons). 

Thanks!
Kenny

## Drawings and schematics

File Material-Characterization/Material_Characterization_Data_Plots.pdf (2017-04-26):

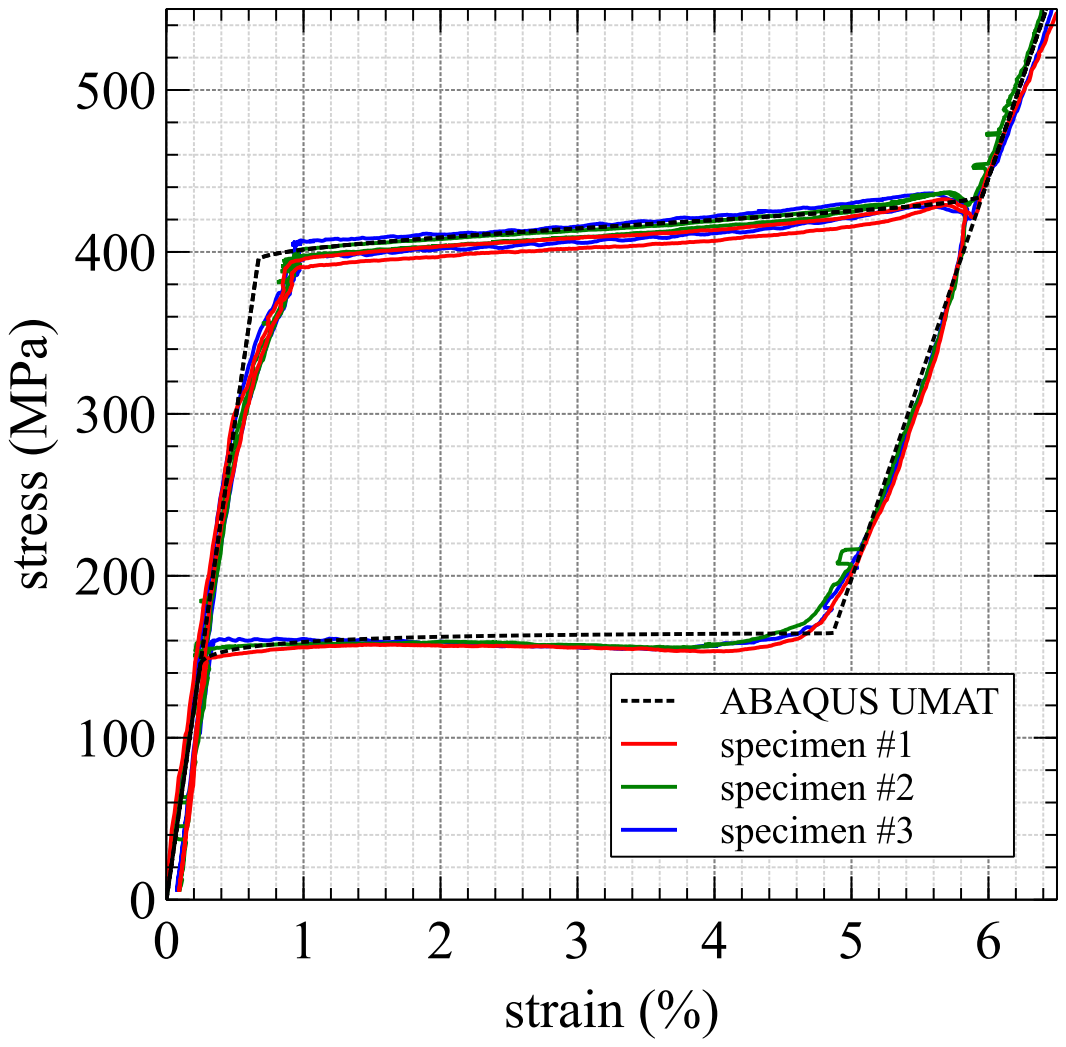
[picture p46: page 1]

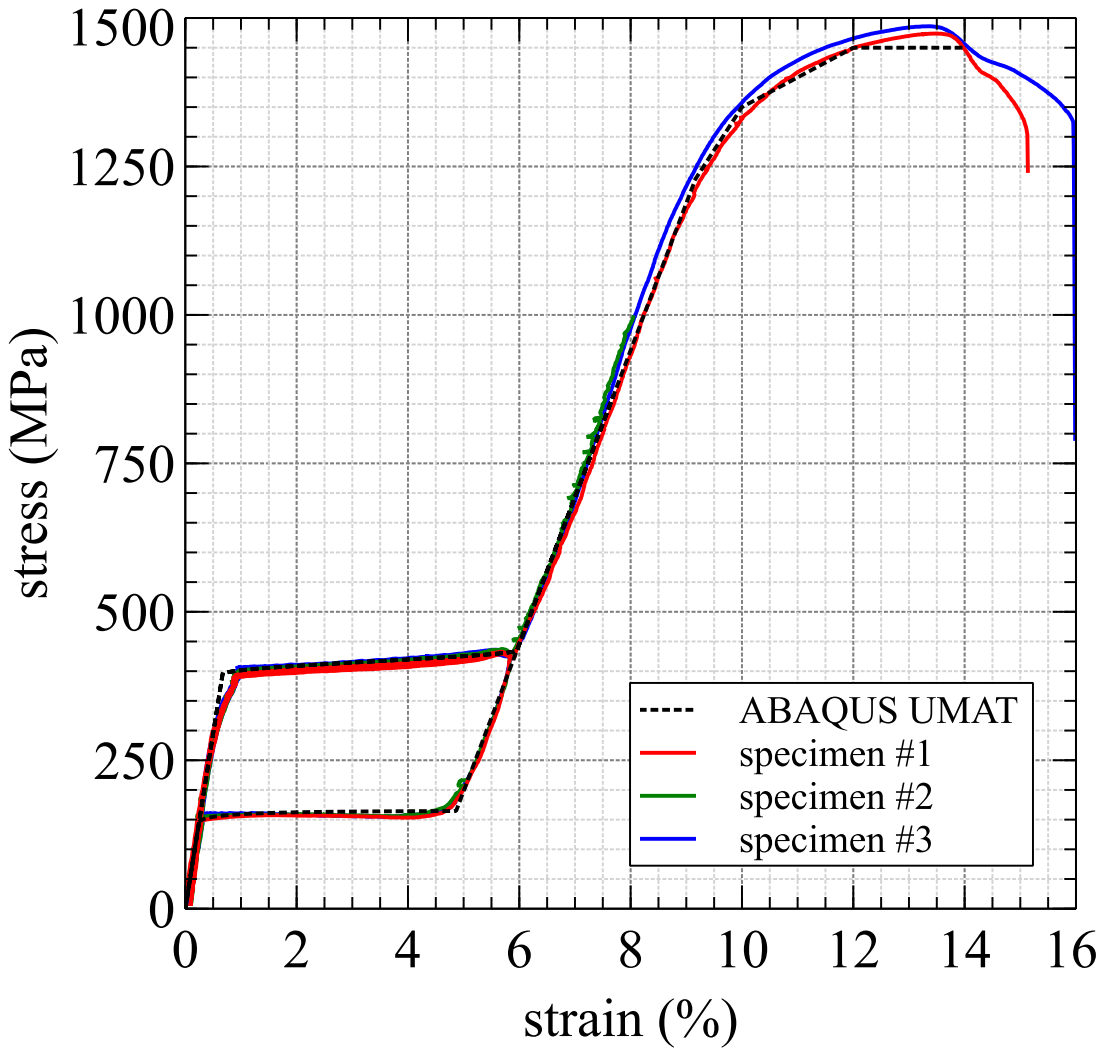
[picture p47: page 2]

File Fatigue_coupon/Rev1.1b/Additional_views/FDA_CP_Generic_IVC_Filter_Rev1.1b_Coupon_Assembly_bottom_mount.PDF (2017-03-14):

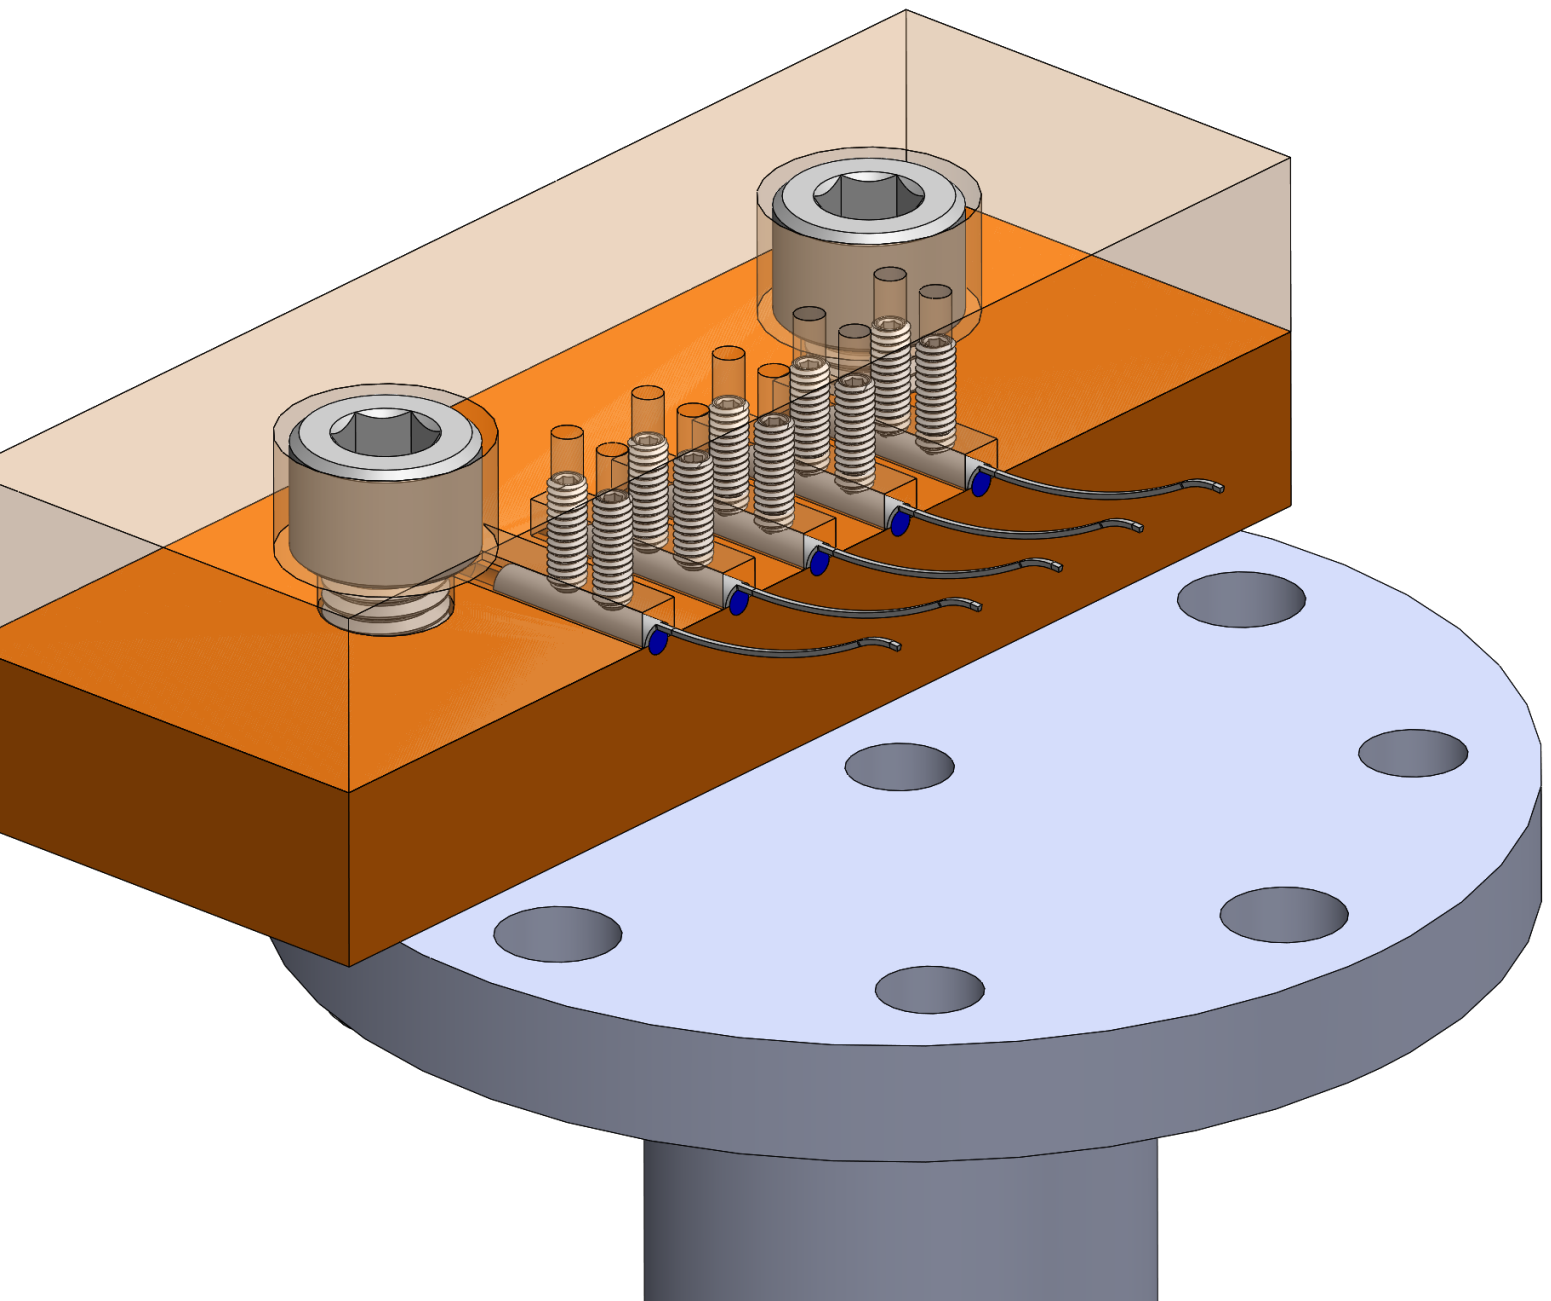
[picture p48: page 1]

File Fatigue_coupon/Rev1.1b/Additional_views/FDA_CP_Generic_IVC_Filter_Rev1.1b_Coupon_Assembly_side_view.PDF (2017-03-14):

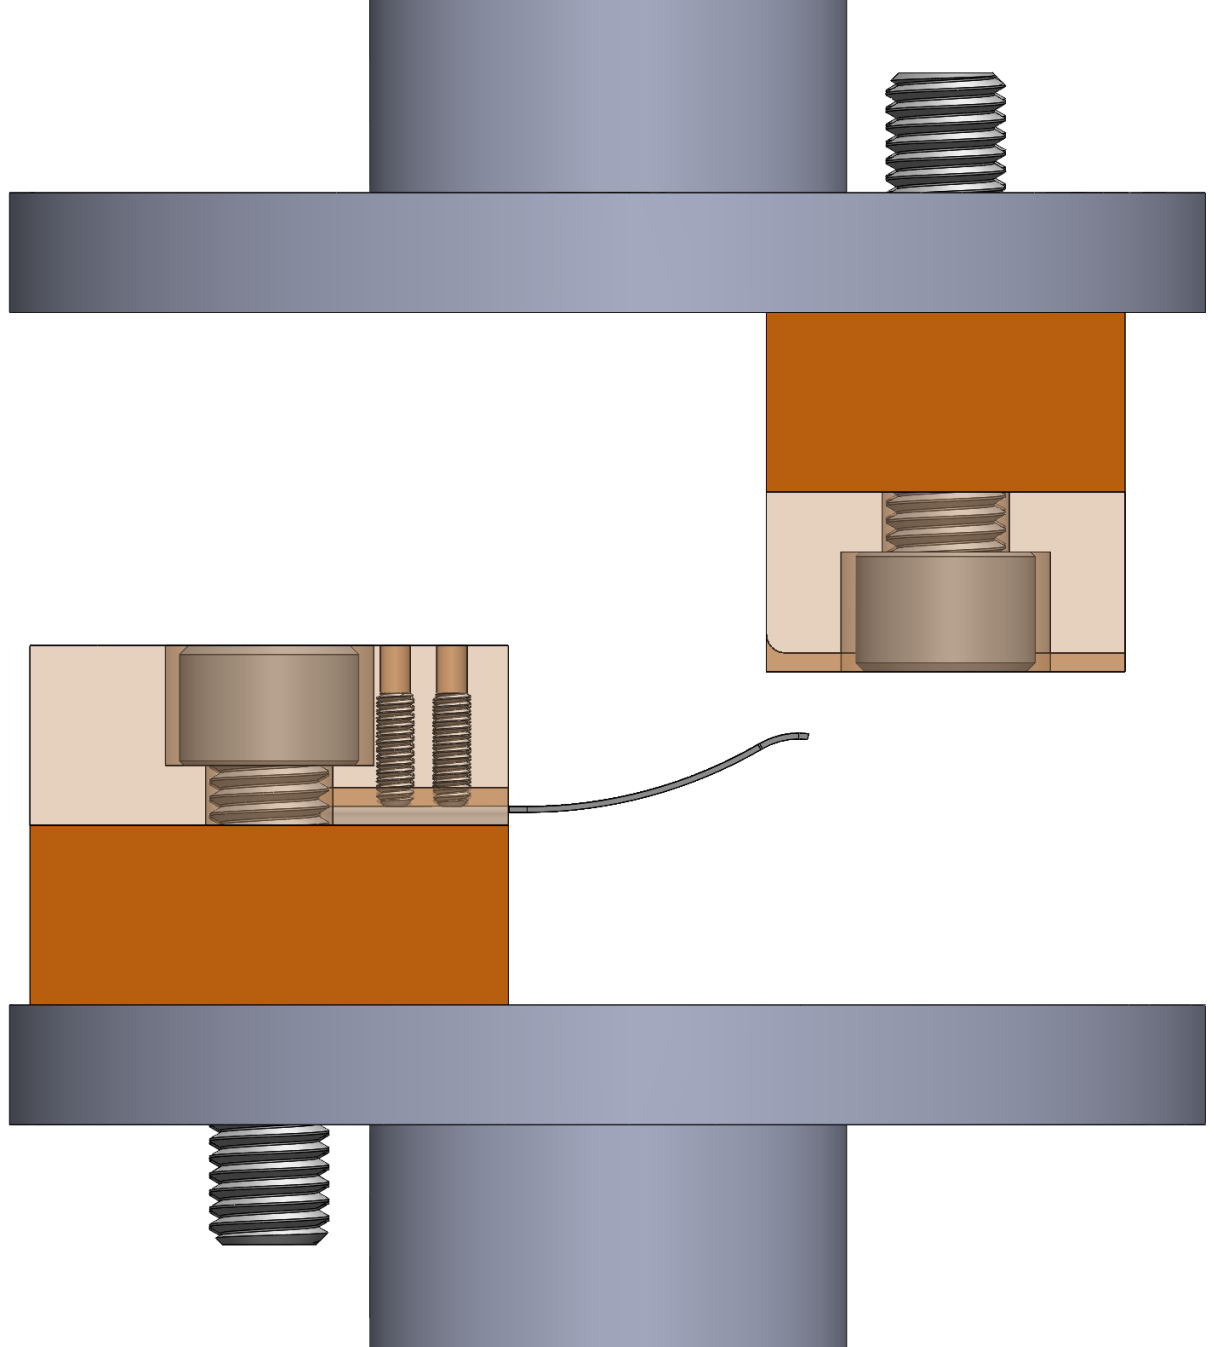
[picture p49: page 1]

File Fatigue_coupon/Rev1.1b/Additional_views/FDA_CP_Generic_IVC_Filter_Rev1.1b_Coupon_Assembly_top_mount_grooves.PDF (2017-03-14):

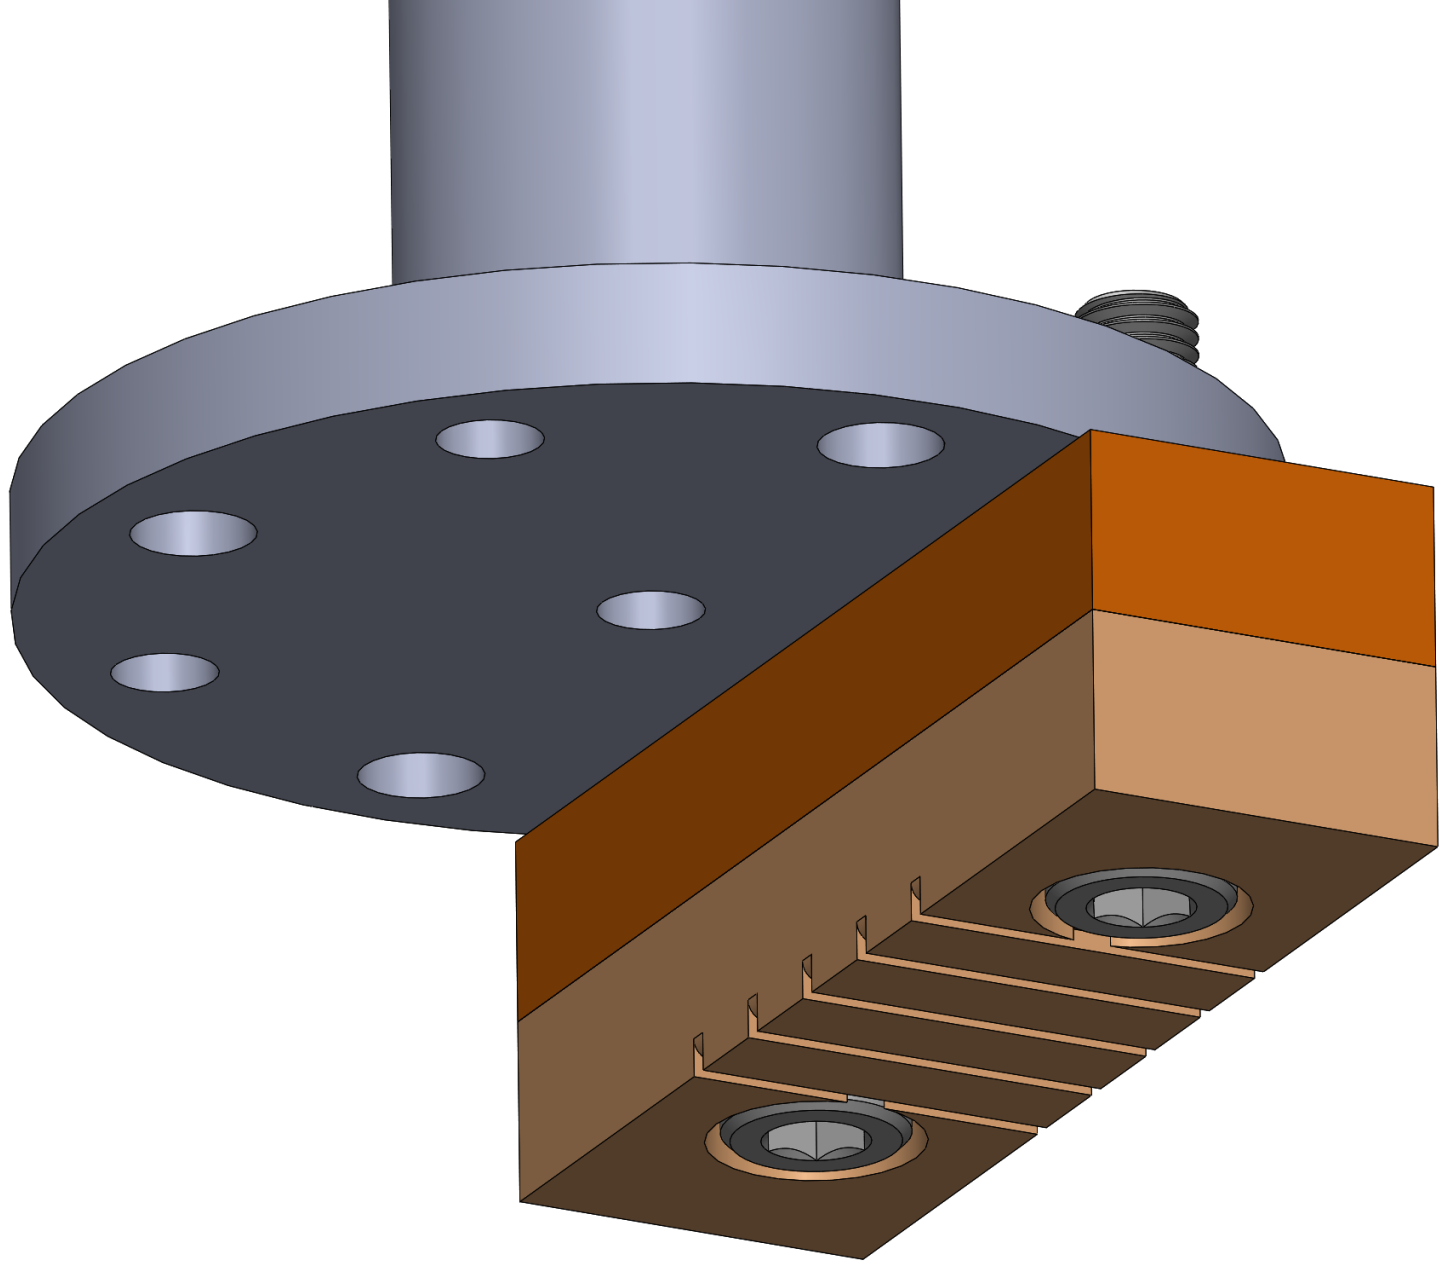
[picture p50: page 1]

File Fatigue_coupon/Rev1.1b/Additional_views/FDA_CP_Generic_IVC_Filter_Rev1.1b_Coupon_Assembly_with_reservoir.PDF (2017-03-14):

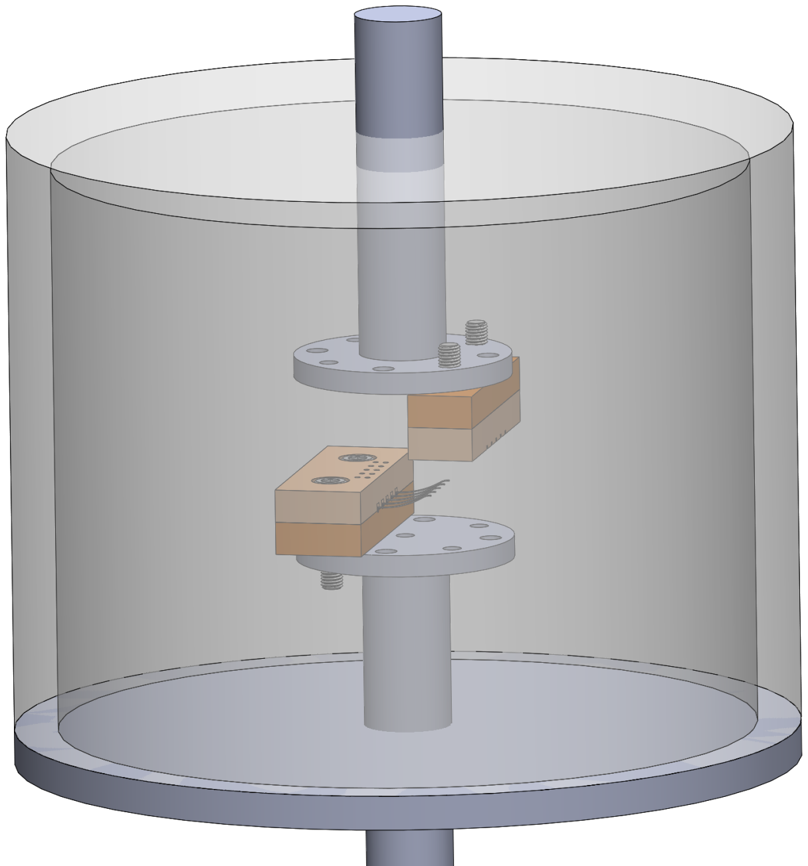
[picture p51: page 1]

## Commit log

2017-01-18 Add files via upload
    CAD Files for "Rev0" and "Rev1" generic IVC filter designs.
    "Rev0": C. Bonsignore, based on drawing from B. Craven
    "Rev1": K. Aycock, after FEA analysis & feedback from group. Ready for generating physical prototype?
    There were multiple Rev0.x versions between "Rev0" and "Rev1"
    [FDA_CP_Generic_IVC_Filter_Rev0.SLDPRT, FDA_CP_Generic_IVC_Filter_Rev1.SLDPRT]
2017-01-23 Add files via upload
    Matches FEA model
    [FDA_CP_Generic_IVC_Filter_Rev1.SLDPRT]
2017-01-23 Move file to new directory
    [FDA_CP_Generic_IVC_Filter_Rev0.SLDPRT, FDA_CP_Generic_IVC_Filter_Rev1.SLDPRT]
2017-01-23 Added ABAQUS FEA files
    [GIVCF_Rev1.STEP]
2017-01-23 Moved 'FEA' directory to 'Preliminary_FEA'
    [GIVCF_Rev1.STEP]
2017-02-01 Add files via upload
    Original concept for generic IVC filter (from August 2016)
    [Mock-IVC-Lumen.iges]
2017-02-01 Moved CAD files into separate folders for each design revision
    [FDA_CP_Generic_IVC_Filter_Rev0.SLDPRT, FDA_CP_Generic_IVC_Filter_Rev1.SLDDRW, FDA_CP_Generic_IVC_Filter_Rev1.SLDPRT]
2017-02-01 Moved ABAQUS/CAE files into their own directory
    [GIVCF_Rev1.STEP]
2017-02-03 Add files via upload
    Uploaded SolidWorks part file and drawing for updated filter.
    The CAD model now accounts for laser kerf and material removal for finishing (e.g., electropolishing)
    [FDA_CP_Generic_IVC_Filter_Rev1.1.SLDDRW, FDA_CP_Generic_IVC_Filter_Rev1.1.SLDPRT]
2017-02-03 Add files via upload
    * Added notes to clarify "as-cut" and "finished" configurations.
    * Added an "as-cut, expanded" configuration
    * Note the "finished" drawings are only placeholders and must be updated based on measurements from finished prototypes. The "finished" drawings are not relevant to manufacturing.
    * The "finished" filter dimensions / filter geometry will be needed for final mathematical and numerical analyses.
    [FDA_CP_Generic_IVC_Filter_Rev1.1.SLDDRW, FDA_CP_Generic_IVC_Filter_Rev1.1.SLDPRT]
2017-02-03 Add files via upload
    (correct small typographical error)
    [FDA_CP_Generic_IVC_Filter_Rev1.1.SLDDRW]
2017-02-04 Add files via upload
    * Changed kerf width to 50 microns (0.050mm)
    * Updated "m_width" to 0.025mm based on discussion with Karthik
    [FDA_CP_Generic_IVC_Filter_Rev1.1.SLDDRW, FDA_CP_Generic_IVC_Filter_Rev1.1.SLDPRT, FDA_CP_Generic_IVC_Filter_Rev1.1_Laser_template.DXF]
2017-02-06 Add files via upload
    Proposed fatigue coupon (corresponds to Rev1.1 full filter design)
    [FDA_CP_Generic_IVC_Filter_Rev1.1_Coupon.DXF, FDA_CP_Generic_IVC_Filter_Rev1.1_Coupon.SLDDRW, FDA_CP_Generic_IVC_Filter_Rev1.1_Coupon.SLDPRT]
2017-02-06 Moved files into folders
    [FDA_CP_Generic_IVC_Filter_Rev1.1_Coupon.DXF, FDA_CP_Generic_IVC_Filter_Rev1.1_Coupon.SLDDRW, FDA_CP_Generic_IVC_Filter_Rev1.1_Coupon.SLDPRT, FDA_CP_Generic_IVC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]
2017-02-09 Add files via upload
    Updated drawing file and included Austenite finish temperature as requested by Craig in https://github.com/kenaycock/Generic-IVC-Filter/issues/3
    [FDA_CP_Generic_IVC_Filter_Rev1.1.SLDDRW]
2017-04-26 Added files for nitinol material characterization
    [IVC Filter Tube 37C_SUMMARY_UMAT_Verification.xlsx]
2017-04-26 Geometry of generic IVC filter placed in 28mm IVC
    Geometry of generic IVC filter placed in 28mm IVC
    - Uses updated feature dimensions (average feature measurements from Karthik)
    - Used updated material model constants (see 'material-characterization' folder, constants from 04/25/2017)
    [IVC_28mm_dia.stl]
2017-04-27 Update material characterization plot
2017-05-15 - Changing directory name for consistency
    [01_low-strain-coupon.DXF, FDA_CP_Generic_IVC_Filter_Rev1.2_low-strain-coupon.SLDDRW]
